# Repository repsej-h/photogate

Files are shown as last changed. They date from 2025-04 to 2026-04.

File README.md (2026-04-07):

Watch the video

# Photogate

## Project description

The photogate project is an Arduino compatible PCB, designed to take precise measurements of for example a pendulum's period or the speed of a miniature car in a test rig. Since the photogate project is driven by a school project, some screenshots and component workings will be included in this repository.

### The PCB

The U-shaped PCB most importantly features a 3 pin connector. From left to right the pins need to be connected to `GND`, `digital interrupt` & `+5V` on your Arduino. There are two mounting holes in the PCB, which could be used to attach the photogate to a 3d printed mounting piece (which is not yet developed). Last every PCB features a unique QR-code, for easy identification of the PCB's

A screenshot of the schematics can by found in the `references` folder

### Components

Only 5 components are placed on the PCB. Starting off with `R1` and `R2`, these are 220 $\Omega$ and 2000 $\Omega$ resistors respectively. These are placed on the board as 0805 SMD **resistors**. Next is a 3 pin connector with a 90 degree bend, making the photogate easily compatible with a breadboard. Alternatively, when mounting the PCB, female to male Arduino jumper wires can be used. Next we have the more vital components. The first one is the 940 nm LED, which constantly emits light when connected to a power source. Finally a 940 nm `insert type`phototransistor either blocks or allows electricity to flow through the circuit. This flow triggers an interrupt request (IRQ)

## Sponsership

Special thanks to [PCBWay](https://www.pcbway.com/) for providing me with quick and easy pcb prototyping! 

Working with them has been nothing but smooth. Their boards are top-notch, their turnaround times are fast, and the entire process is incredibly easy from start to finish. Whether you're prototyping something new or scaling up for production, they make sure you get exactly what you need — quickly and reliably.

If you are interested in ordering some photogates, I highly recommend checking them out via [this link](https://www.pcbway.com/project/shareproject/Arduino_Photogate_PCB_ff1ebb34.html).
PCBway logo

# Scripts

Currently the photogate project features 3 scripts:

## photogate.ino

This script uses a single photogate pcb to measure the time between two triggers.
For demonstration purposes, the internal arduino led is turned on in between the start and stop trigger.
A picture of the hardware setup is presented below. In order for the interrupt to work, the `SensorPin` **has to be wired** to the `digital 2 / 3` pin on an Arduino Uno. (cfr interrupts)



## photogate_pendulum.ino

This script is used to measure the period of a pendulum using a single photogate. It calculates the high-precision average of 10 measured periods to ensure experimental accuracy.

### Key Features

- **Automatic Data Reset:** The script features an sanity check. If the interval between triggers exceeds **5 seconds** (5000 ms), the script assumes the experiment has been paused or adjusted. It will automatically discard previous partial measurements and restart the count from zero.

- **Smooth Table Output:** Data is printed to the Serial Monitor in a strictly aligned table format. This includes:
  
  - **Time:** Padded numerical values to prevent column shifting.
  
  - **Progress Bar:** A visual representation of how many readings are left before the average is calculated.

### Hardware Setup

In order for the timing interrupt to work correctly, the **SensorPin** must be wired to a pin capable of handeling interrupts.

- **Arduino Uno:** Connect to **Digital Pin 2** or **Digital Pin 3**.

### How to Use

1. Connect the hardware as described above.

2. Upload the script and open the **Serial Monitor** (set to **9600 Baud**).

3. Release the pendulum. The first pass will initialize the timer.

4. The table will populate automatically. If you stop the pendulum for more than 5 seconds, the table will reset itself for your next trial.

5. After 10 periods, the final average (T×2) will be displayed in a result block.



## SlingerPeriode.ino

This script has the same functionality as the `photogate_pendulum.ino` script, but has been modified to be used on a college information day. Most important changes are reformatting the script's output and adding instructions for the demo in de code documentation. Also, this script is based on a older version of the pendulum script and still uses analog readings. Theirfore connect the `SensorPin` to pin `A0`!

## speed_measurement.ino

This script is designed to calculate the speed of an object traveling through multiple photogates. Unlike previous projects, an array of photogates is used to collect timestamps along the path of the object. This data is used to calculate the speed of the object for each interval.

> [!NOTE]
> Since old Arduino Uno's only feature 2 interupt pins, only 2 photogates can be used. Please consult [Arduino docs](https://docs.arduino.cc/language-reference/en/functions/external-interrupts/attachInterrupt/) to check if your Arduino model can support more than 2 interrupts.

### Configure the script

By default the script is configured to work with two photogates, connected to digital pins `2` & `3`.  In this case, simply input the distance in cm between the 2 gates right here: `unsigned int distances[pinsLength - 1] = {100};`

When adding more photogates, first add your pins into the `int pins[]` seperatedby comma's. Next plug in the distances between the gates, also separated by comma's into `unsigned int distances[pinsLength - 1]` and you are good to go. 

Until now the script has been tested with up to 3 photogates. Also note that the script doesn't bother in which order gates get triggered. This means that a set up can be used in both directions. The end user needs to interpret which is gate one, two, etc based on the object's trajectory.

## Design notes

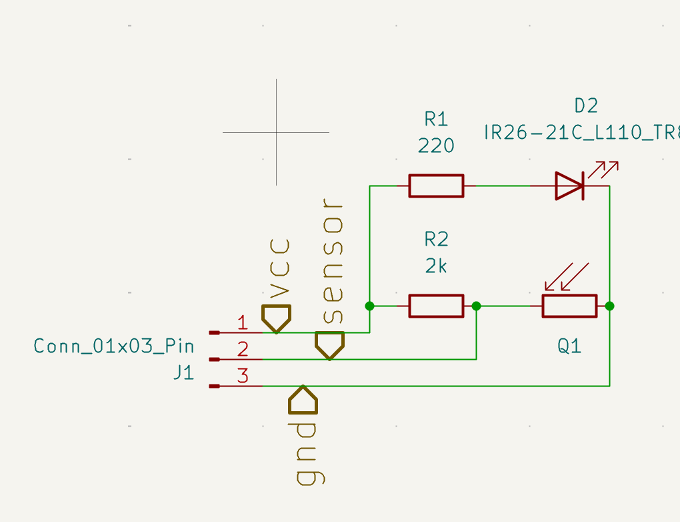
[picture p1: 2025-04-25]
references/schematic.png

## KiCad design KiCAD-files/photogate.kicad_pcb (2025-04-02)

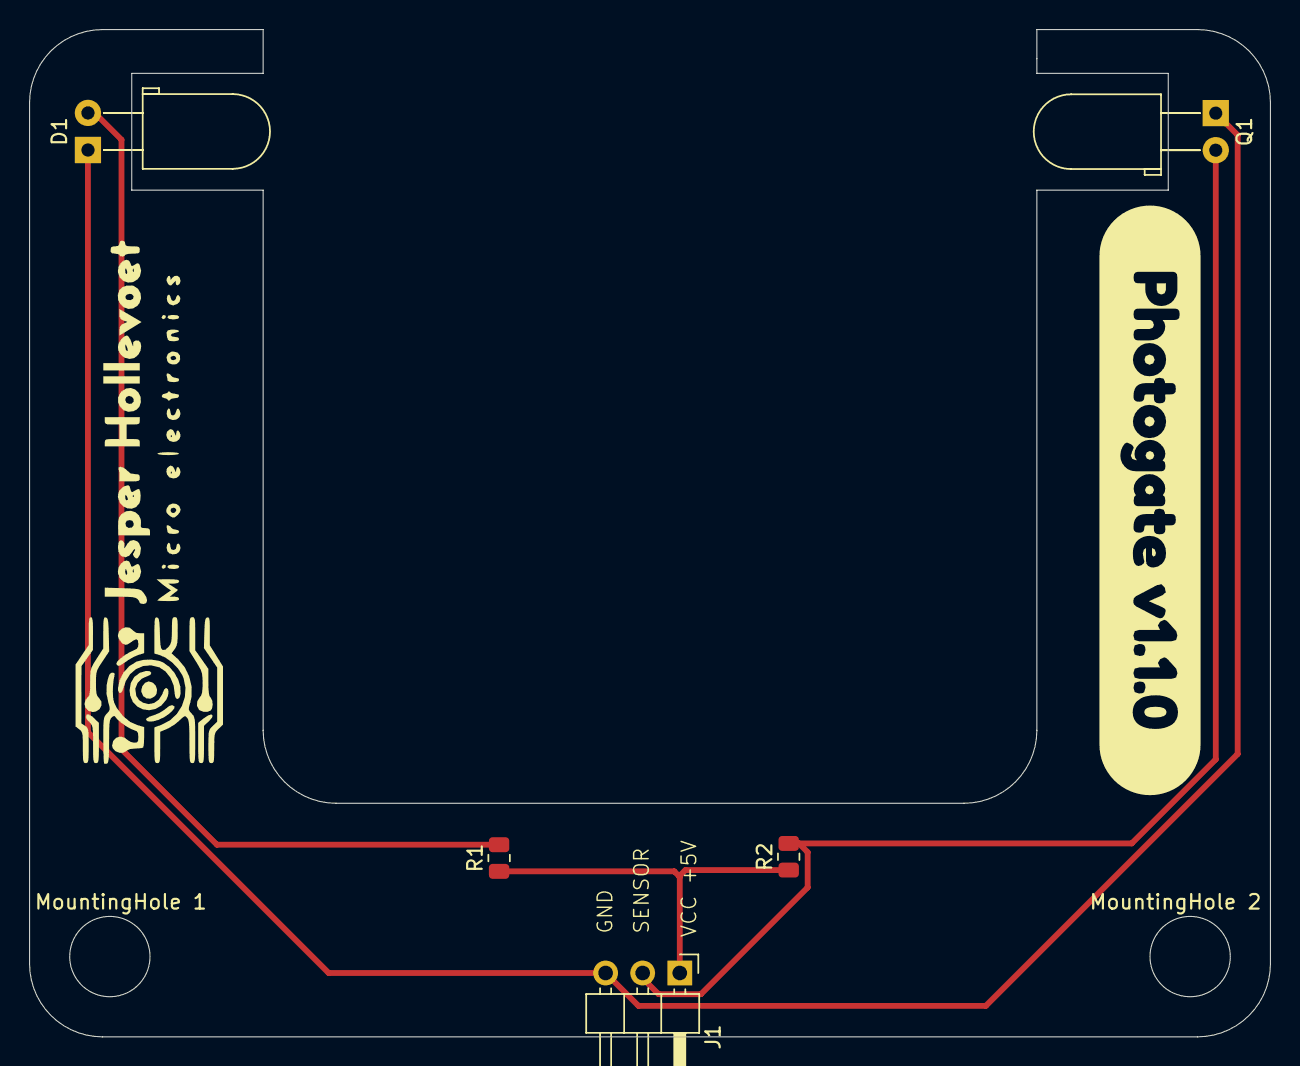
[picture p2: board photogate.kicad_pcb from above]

Board: 2 copper layers, 85.0 x 69.0 mm, 8 parts (0 on the bottom side), 4 nets.

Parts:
D1: IR26-21C_L110_TR8; LED_D5.0mm_Horizontal_O3.81mm_Z3.0mm
J1: Conn_01x03_Pin; PinHeader_1x03_P2.54mm_Horizontal
MountingHole 1, MountingHole 2: MountingHole; MountingHole_5.5mm
Q1: Q1; LED_D5.0mm_Horizontal_O3.81mm_Z3.0mm
R1: 220; R_0805_2012Metric
R2: 2k; R_0805_2012Metric
kibuzzard-67ED3B28: G***; kibuzzard-67ED3B28

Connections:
/gnd: D1.1 (K), J1.3, Q1.1
/sensor: J1.2, Q1.2, R2.2
/vcc: J1.1, R1.1, R2.1
unnamed: D1.2 (A), R1.2

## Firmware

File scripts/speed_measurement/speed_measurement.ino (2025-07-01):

// sensorpins
int pins[] = {2, 3}; // Add all sensor pins here.
const int pinsLength = sizeof(pins) / sizeof(pins[0]); // Number of pins - please add a array.length function

// Distances between consecutive photogates in cm.
// For N photogates, there are N-1 intervals.
unsigned int distances[pinsLength - 1] = {100}; // Example: 100cm between pin 2 and pin 3. Adjust if you add more pins/intervals.

// Store millis() timestamp when each photogate is triggered.
volatile unsigned long times[pinsLength];

// Flag set true when all photogates are triggered.
volatile bool trigger = false;

// Tracks how many photogates have been triggered.
volatile int counter = 0;

void setup() {
  Serial.begin(9600);
  Serial.println("Photogate system initializing...");

  // Set up sensors and attach interrupts.
  for (int i = 0; i < pinsLength; i++) {
    pinMode(pins[i], INPUT);
    attachInterrupt(digitalPinToInterrupt(pins[i]), triggered, RISING);
    Serial.print("Attached interrupt to Pin: ");
    Serial.println(pins[i]);
  }

  pinMode(LED_BUILTIN, OUTPUT);
  Serial.println("Photogate system ready.");
}

void loop() {
  if (trigger) {
    // Disable interrupts to safely copy 'times' array.
    noInterrupts();
    unsigned long localTimes[pinsLength];
    for (int i = 0; i < pinsLength; i++) {
      localTimes[i] = times[i];
    }
    interrupts(); // Re-enable interrupts.

    // Calculate speeds for each interval.
    for (int i = 1; i < pinsLength; i++) {
      unsigned long intervalTimeMs = localTimes[i] - localTimes[i - 1];

      if (intervalTimeMs > 0) {
        unsigned int intervalDistanceCm = distances[i - 1];
        float speedMps = (float)intervalDistanceCm / intervalTimeMs * 10.0;

        Serial.print("Speed between gate ");
        Serial.print(i);
        Serial.print(" and gate ");
        Serial.print(i + 1);
        Serial.print(":\t");
        Serial.print(speedMps, 3);
        Serial.println(" m/s");
      } else {
        Serial.print("Error: Interval time for gate ");
        Serial.print(i);
        Serial.println(" was zero.");
      }
    }

    Serial.println("--- Measurement Complete ---");

    // Reset for the next measurement.
    trigger = false;
    counter = 0;
  }

  delay(10);
}

// Interrupt Service Routine (ISR)
void triggered() {
  if (counter < pinsLength) {
    times[counter] = millis();
    counter++;
  }

  if (counter == pinsLength) {
    trigger = true;
  }
}

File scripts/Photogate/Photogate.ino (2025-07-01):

#define SensorPin 2 

//variables for time interval
bool timing = false;
unsigned long deltaT = 0;
unsigned long startT = 0;
unsigned long stopT = 0;
const int threshold = 200; // can be adjusted according to light levels; remove // on line 38 to print light level to console

volatile bool trigger = false;

void setup() {
  Serial.begin(9600); // sets serial port for communication
  Serial.println("Photogate up and running");

  // set up sensor
  pinMode(SensorPin, INPUT);
  attachInterrupt(digitalPinToInterrupt(SensorPin), triggered, RISING);

  // set up build in led
  pinMode(LED_BUILTIN, OUTPUT); 
}

void loop() {
  if (trigger){   
    if (!timing){
      timing = true;
      startT = millis();
      Serial.println("Sensor triggerd, timer started");
      digitalWrite(LED_BUILTIN, HIGH); // turn on led when timing
    } else {
      Serial.println("Sensor triggerd, timer stopped");
      stopT = millis();
      deltaT = stopT - startT;
      Serial.print("Time Elapsed: ");
      Serial.println(deltaT);
      timing = false;
      digitalWrite(LED_BUILTIN, LOW); // turn off led when done
    }
    trigger = false;
  }
  delay(10);
  
}

void triggered(){
  trigger = true;
}

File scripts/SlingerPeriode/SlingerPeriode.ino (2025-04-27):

#define SensorPin A0

// variables for sensor state
int SensorValue = 0;
int preSensorValue = 0;

//variables for time interval
bool timing = false;
unsigned long deltaT = 0;
unsigned long startT = 0;
unsigned long stopT = 0;
const int threshold = 200; // can be adjusted according to light levels; remove // on line 26 - 27 to print light level to console



int periodCount = 0; // Keep track of how many periods have been recorded
float average = 0;  
const int counts = 10; // amout of periods before calculating the average
unsigned long periods[counts];

void setup() {
  Serial.begin(9600); // Initialize serial communication
}

void loop() {
  SensorValue = analogRead(SensorPin); // Read the current value of the sensor

  // Print the light level for debugging or adjustment of the threshold
  // Serial.print("Sensor Value: ");
  // Serial.println(SensorValue);

  if (SensorValue > threshold && preSensorValue < threshold) { // switch state: no light reaching sensor after a period of light reaching the sensor
    if (!timing) {
      timing = true;
      startT = millis();
    } else if (periodCount < counts) { // Record period only if the array is not full
      stopT = millis();
      deltaT = stopT - startT;

      Serial.print("Meting ");
      Serial.print(periodCount + 1);
      Serial.print("\t");

      periods[periodCount] = deltaT;
      startT = stopT;
      periodCount++; 

      if(deltaT < 2000){
        Serial.print("Time Elapsed: ");
        Serial.print(deltaT);
        Serial.println(" ms");
      }

      // Calculate and print the average only after x periods
      if (periodCount == counts) {
        unsigned long sum = 0;
        for (int i = 0; i < periodCount; i++) {
          if (periods[i] < 2000){
            sum += periods[i];
          }
          
        }

        average = (float)sum *2 / (periodCount*1000);
        Serial.print("Periode (after 10 periods): ");
        Serial.print(average,2);
        Serial.println(" s \n\n\n\n");
        

        delay(5000);
        // Reset the period count for the next set of x periods
        periodCount = 0;

      }
    }
  }

  preSensorValue = SensorValue; // Update the previous sensor value
  delay(10); // Small delay to avoid rapid readings
}
/*



Denk je dat de slingerperiode (de tijd voor één heen- en weergaande beweging) veel beïnvloed wordt door de hoogte van waarop de slinger losgelaten wordt?
DOE de test hier. Laat de slinger los vanaf een welbepaalde hoogte. De opstelling voert 10 metingen uit en geeft je het gemiddelde.
HERHAAl de test, maar laat nu log vanaf een grotere of kleinere hoogte.
MAAK de hoek nooit groter dan 70°.


*/

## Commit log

2025-04-02 V1 final touches
    [photogate.kicad_pcb, photogate.kicad_sch]
2025-04-02 adding revision so kicad export script works
    [photogate.kicad_pcb, photogate.kicad_sch]
2025-04-24 Moving KiCAD files to folder & adding scripts folder
    [photogate.kicad_pcb, photogate.kicad_sch]
2025-04-25 add project and pcb description
2026-04-07 print tabel header before each new measurement
